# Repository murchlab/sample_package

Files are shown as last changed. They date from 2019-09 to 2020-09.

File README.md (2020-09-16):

# Sample Package v1.3

## Purchase list

1. Copper rod stock

    Superconducting 101 copper rod, Diameter = 1.5"

    https://www.mcmaster.com/8965k75

2. Screws for fastening (4 for each)

    \#4-40 Brass socket head screw, Length = 5/8"

    https://www.mcmaster.com/93465a111

3. Screws for mounting (2 for each)

    \#4-40 Brass Pan Head Phillips Screws, Length = 1"

    https://www.mcmaster.com/94070a115

4. Nuts for mounting (2 for each)

    \#4-40 Brass hex nut, Width = 1/4", Height = 3/32"

    https://www.mcmaster.com/92671a005

5. Screws for thermalization (1 for each)

    \#4-40 Brass socket head screw, Length = 1/4"

    https://www.mcmaster.com/93465a106
    
## Milling procedures

These G-code files are generated in a certain order. Particularly, I assume that the milling procedures are performed before the drilling ones.

#### The way I name the files:

1. The first letter:

        x: Stands for the top part
        y: Stands for the bottom part
        
2. The second letter:

        t: Stands for the topside of the part
        b: Stands for the bottomside of the part
        
3. Letter "c" indicates that this file is for center drills

4. The numbers indicats the tool to use.

### Top, Topside

1. Pockets: 3/32" End Mill

        xt332.txt

2. Center Drills

        xtc43.txt (Z = -0.015")
        xtc32.txt (Z = -0.135")
        xtc3mm.txt (Z = -0.135")
        
3. \#4-40 tapped holes: #43 Drill Bit

        xt43.txt (Z = -0.620")

4. \#4-40 close fit: #32 Drill Bit

        xt32.txt (Z = -0.620")

5. \#4-40 mounting holes: 3mm Drill Bit

        xt3mm.txt (Z = -0.620")
          
### Top, Bottomside

1. The pocket: 3/32" End Mill

        xb332.txt
        
### Bottom, Topside

1. Open pocket: 3/8"" End Mill

        yt38.txt

2. Pockets: 3/32" End Mill

        yt332.txt

3. Center Drills

        ytc45.txt (Z = -0.015")
        ytc43.txt (Z = -0.055")
        ytc2p3.txt (Z = -0.105")
        ytc3mm.txt (Z = -0.055")

4. Post pockets: #45 Drill Bit

        yt45.txt (Z = -0.0667")
        
5. \#4-40 tapped holes: #43 Drill Bit

        yt43.txt (Z = -0.300")
        
6. Coaxial holes: #42 Drill BIt

        yt40.txt (Z = -0.300")
        
7. \#4-40 mounting holes: 3mm Drill Bit

        yt3mm.txt (Z = -0.300")

### Bottom, Bottomside

1. Pockets: 3/32" End Mill

        yb332.txt

## Guidelines for CNC machining (Bridgeport EZTrak)

### Workflow
    
1. Design the part using SolidWorks.

2. Generate the toolpaths using the built-in SolidWorks CAM.

3. Generate the G-code files using a post processor named "EZTRAK_G.ctl". One G-code file corresponding to one toolpath only (without tool change operations).

4. Use the python scripts to modify the generated G-code files.

### Compatibility

The machine is old, which means certain G-code commands are not recognized by this machine. The known examples include:
  
1. Drilling commands like G81, G83

2. Tool radius compensation commands like G40, G41

In order to bypass these commands, we use python scripts to modify the G-code files generated by the default "Drill" and "Center Drill" operations in SolidWorks CAM.

### Milling

We do both roughing & finishing procedures.

1. Spindle

        Spindle Speed = 2400 rpm

2. Feedrates:

        XY Feedrate = 8 in/min
    
        Z Feedrate = 4 in/min
        
        Leadin Feedrate = 4 in/min
    
3. Side parameters:
    
        Allowance = 0.01 in
        
        Stepover = 80%
      
        Wedge Machining: True
      
4. Depth parameters:

    a. For roughing

        Bottom Allowance = 0 in
    
        Island Allowance = 0 in
    
        First Cut Amount = 0.02 in
    
        Max Cut Amount = 0.02 in
    
        Final Cut Amount = 0.01 in
        
    b. for finishing
    
        Allowance = 0 in
    
        First Cut Amount = 10 in
    
        Max Cut Amount = 10 in
    
        Final Cut Amount = 0 in
        
        (The value "10 in" can be as large as possible)

5. NC

        CNC Compensation: OFF
        
        (This prevents the program from producing G40 and G41 codes.)
        
### Drilling

We do centering before drilling. G-code file for both procedures are modified by the python script "modify_gcode.py". Spindle and feedrate parameters are the same as used in the milling procedures.

1. Center Drill

        Center Drill Depth = 0.015 in

2. Drill

        Add Tip Length: True
        
3. Pecking (This parameter is defined in the python file "gcode-tools.py")

        Pecking Depth = 0.050"

## Related projects

1. A new sample rack and a new copper bucket for our new fridge

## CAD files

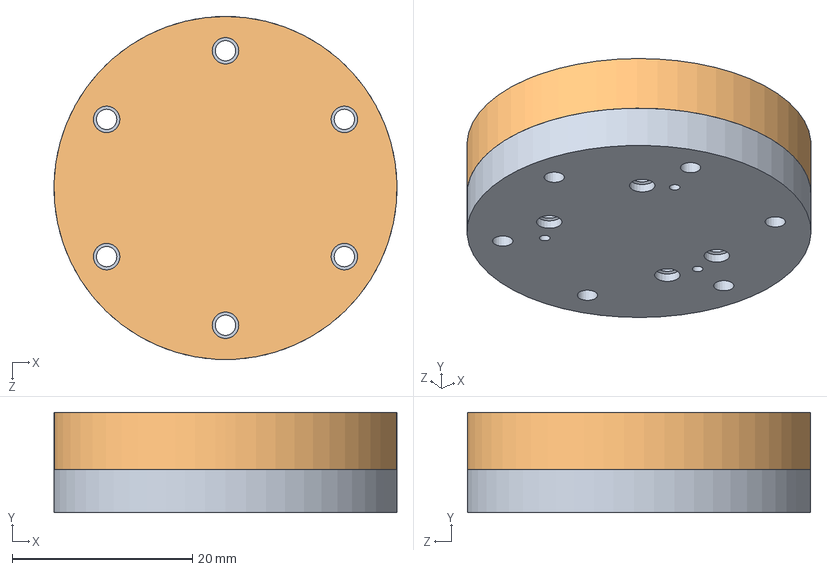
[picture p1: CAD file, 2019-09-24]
Assembly.SLDASM
38.1 x 11.1 x 38.1 mm
Bottom
Top

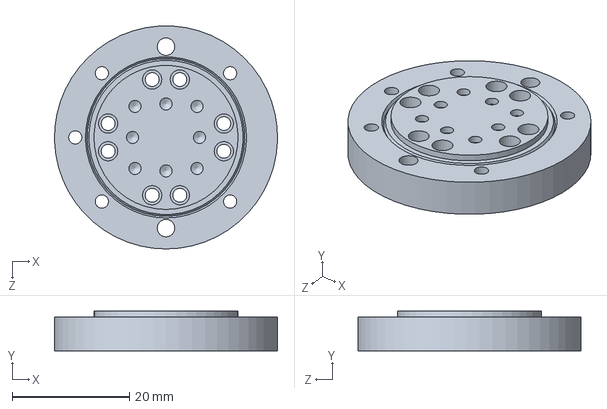
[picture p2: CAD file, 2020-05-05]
Bottom.SLDPRT
38.1 x 6.81 x 38.1 mm

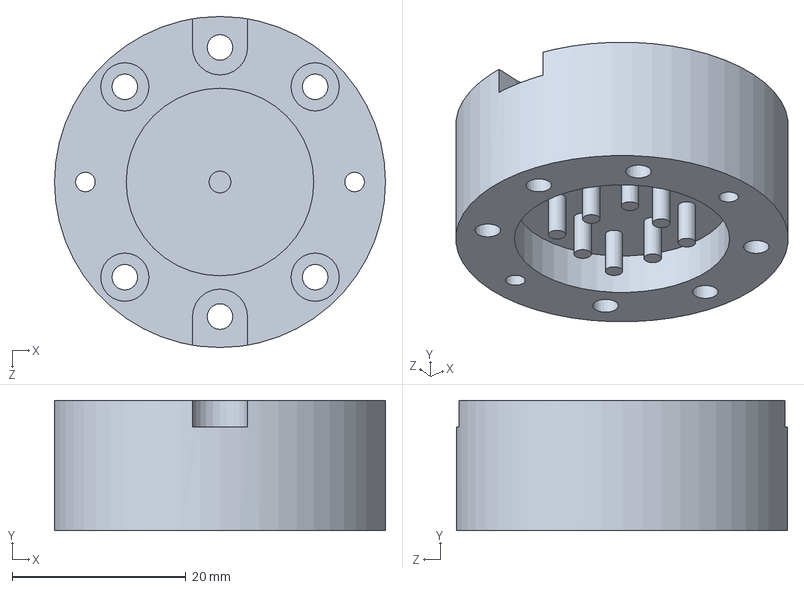
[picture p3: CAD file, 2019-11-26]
Top.SLDPRT
38.1 x 15.0 x 38.1 mm

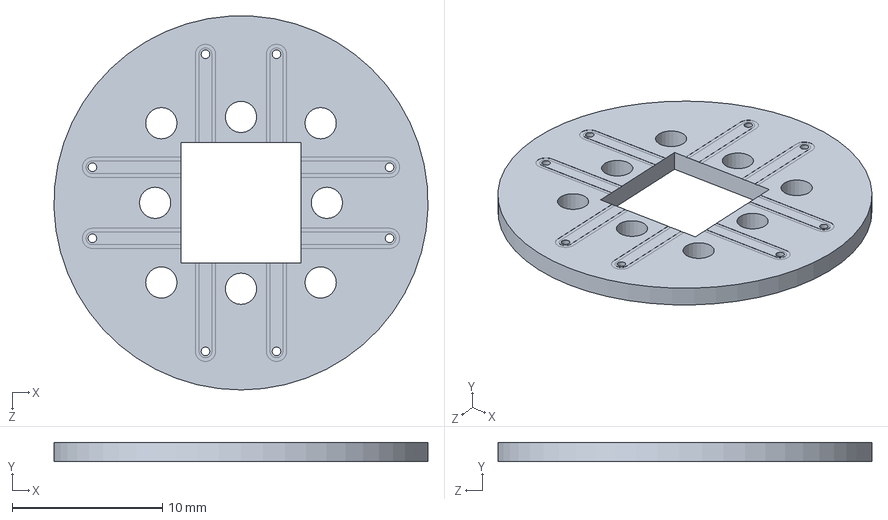
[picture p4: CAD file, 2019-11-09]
Dielectric.SLDPRT
24.9 x 1.29 x 24.9 mm

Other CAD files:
sample_package.SLDDRW

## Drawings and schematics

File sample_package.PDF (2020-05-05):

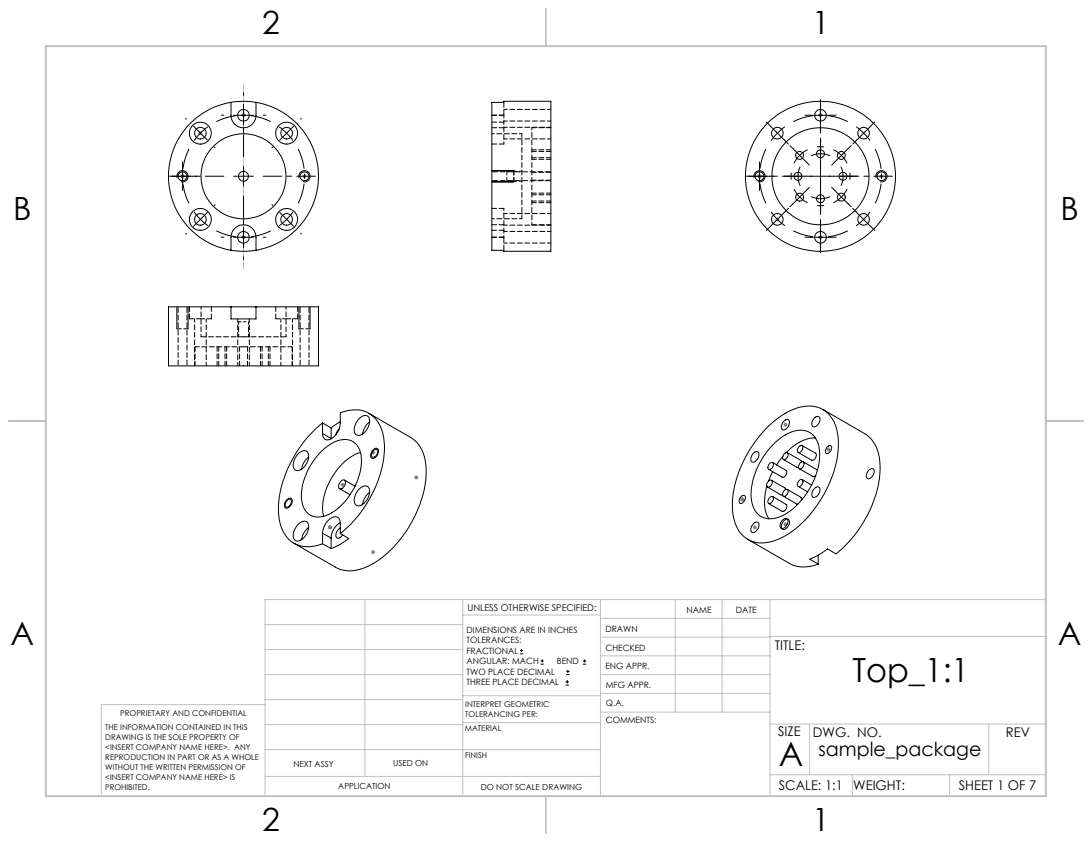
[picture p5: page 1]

UNLESS OTHERWISE SPECIFIED: | | NAME | DATE
DIMENSIONS ARE IN INCHES TOLERANCES: FRACTIONAL ANGULAR: MACH BEND TWO PLACE DECIMAL THREE PLACE DECIMAL | DRAWN

CHECKED | | | TITLE: Top_1:1

ENG APPR.
MFG APPR.

INTERPRET GEOMETRIC TOLERANCING PER: | Q.A.
MATERIAL | | SIZE A | DWG. NO. sample_package | REV

PROPRIETARY AND CONFIDENTIAL
THE INFORMATION CONTAINED IN THIS
DRAWING IS THE SOLE PROPERTY OF
<INSERT COMPANY NAME HERE>. ANY
REPRODUCTION IN PART OR AS A WHOLE
WITHOUT THE WRITTEN PERMISSION OF
<INSERT COMPANY NAME HERE> IS
PROHIBITED.

NEXT ASSY | USED ON | FINISH

APPLICATION | DO NOT SCALE DRAWING | | SCALE: 1:1 | WEIGHT: | SHEET 1 OF 7

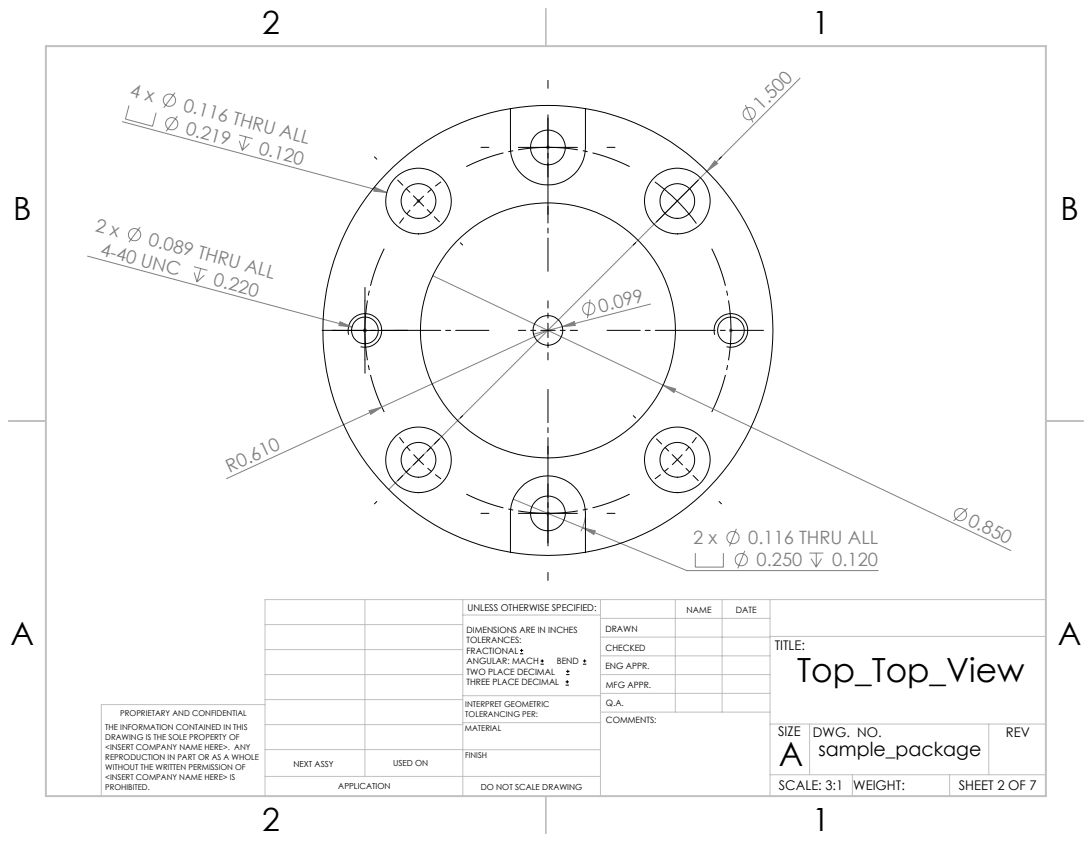
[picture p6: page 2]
2 x 0.089 THRU ALL 4-40 UNC 0.220; 4 x 0.116 THRU ALL 0.219 0.120; 0.116 THRU ALL

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

CHECKED | | | TITLE: Top_Top_View

ENG APPR.
MFG APPR.

INTERPRET GEOMETRIC TOLERANCING PER: | Q.A.
MATERIAL | | SIZE A | DWG. NO. sample_package | REV

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

NEXT ASSY | USED ON | FINISH

SCALE: 3:1 | WEIGHT:

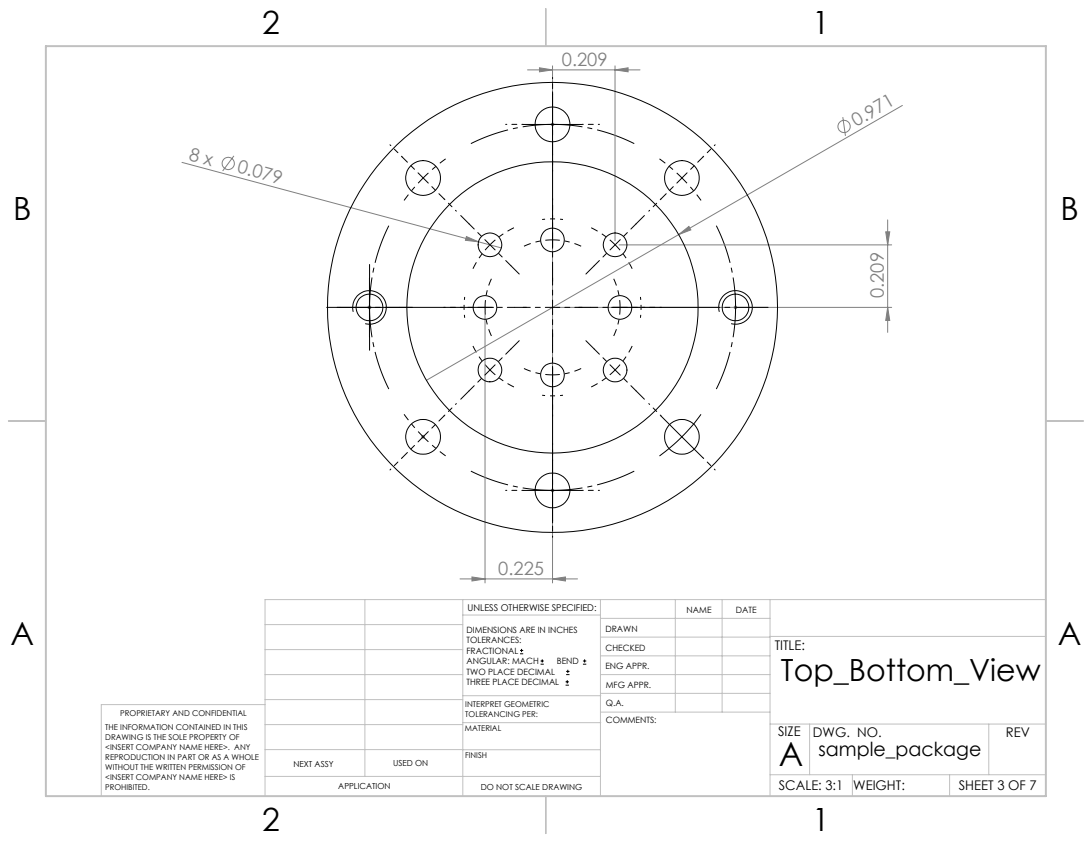
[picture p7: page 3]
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

CHECKED | | | TITLE: Top_Bottom_View

ENG APPR.
MFG APPR.

INTERPRET GEOMETRIC TOLERANCING PER: | Q.A.
MATERIAL | | SIZE A | DWG. NO. sample_package | REV

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

NEXT ASSY | USED ON | FINISH

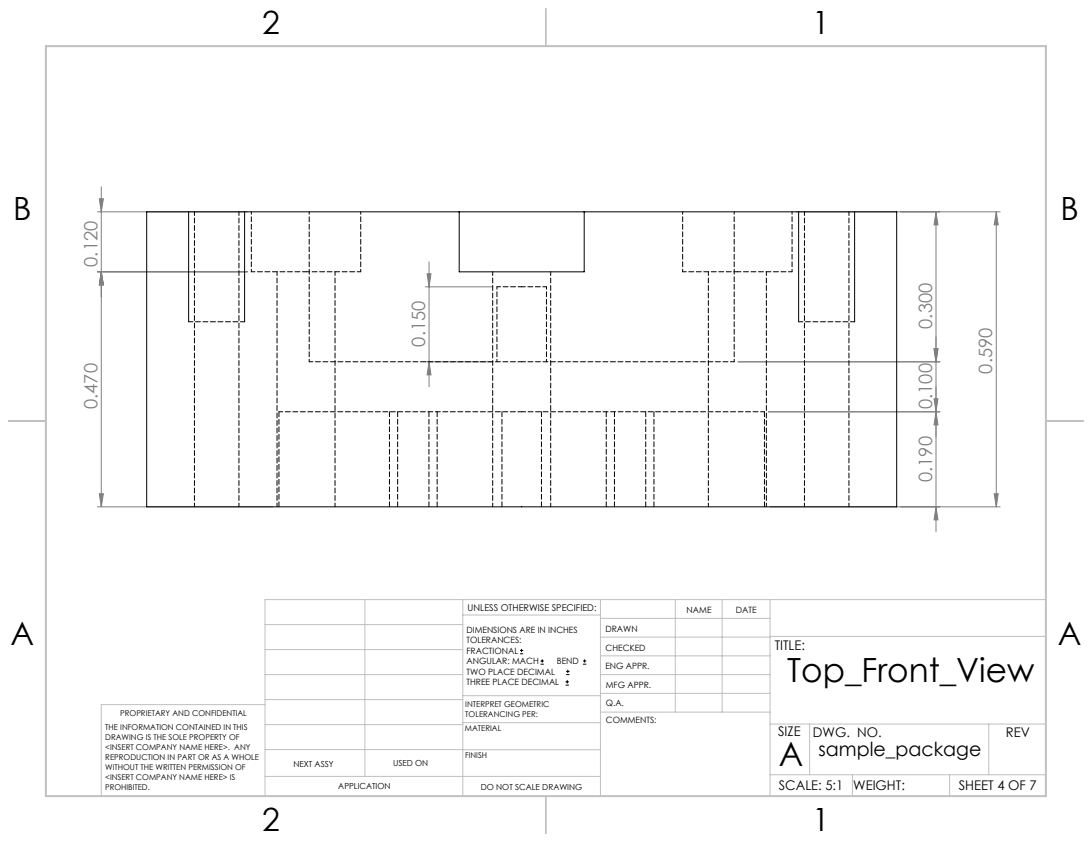
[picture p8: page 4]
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

CHECKED | | | TITLE: Top_Front_View

ENG APPR.
MFG APPR.

INTERPRET GEOMETRIC TOLERANCING PER: | Q.A.
MATERIAL | | SIZE A | DWG. NO. sample_package | REV

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

NEXT ASSY | USED ON | FINISH

SCALE: 5:1 | WEIGHT:

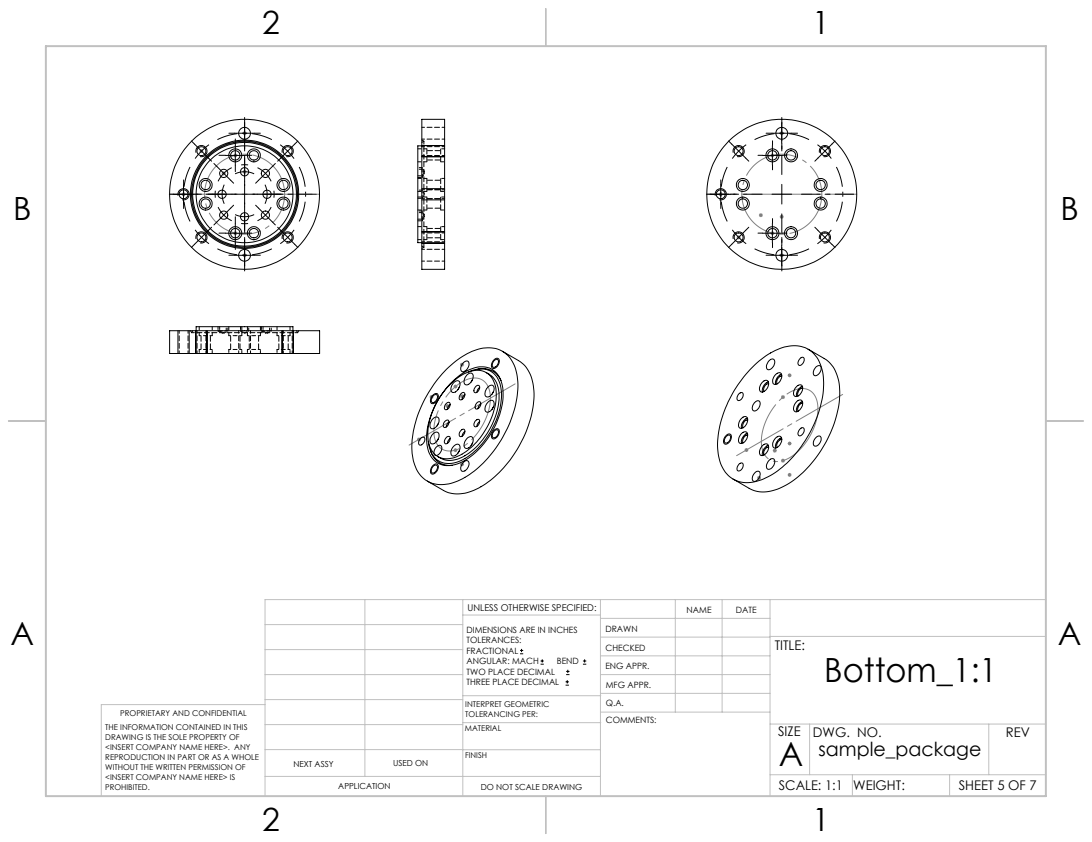
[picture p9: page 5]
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

CHECKED | | | TITLE: Bottom_1:1

ENG APPR.
MFG APPR.

INTERPRET GEOMETRIC TOLERANCING PER: | Q.A.
MATERIAL | | SIZE A | DWG. NO. sample_package | REV

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

NEXT ASSY | USED ON | FINISH

SCALE: 1:1 | WEIGHT:

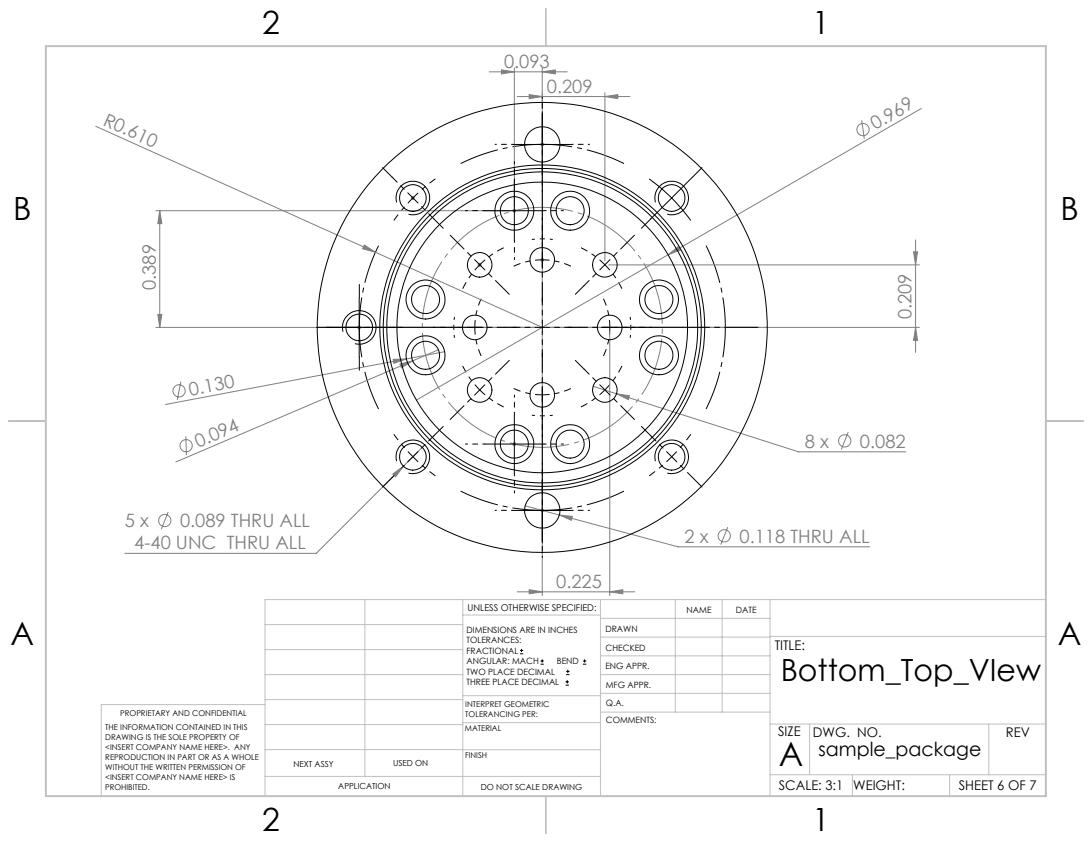
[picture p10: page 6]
0.118 THRU ALL; 0.089 THRU ALL

4-40 UNC THRU ALL

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

CHECKED | | | TITLE: Bottom_Top_VIew

ENG APPR.
MFG APPR.

INTERPRET GEOMETRIC TOLERANCING PER: | Q.A.
MATERIAL | | SIZE A | DWG. NO. sample_package | REV

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

NEXT ASSY | USED ON | FINISH

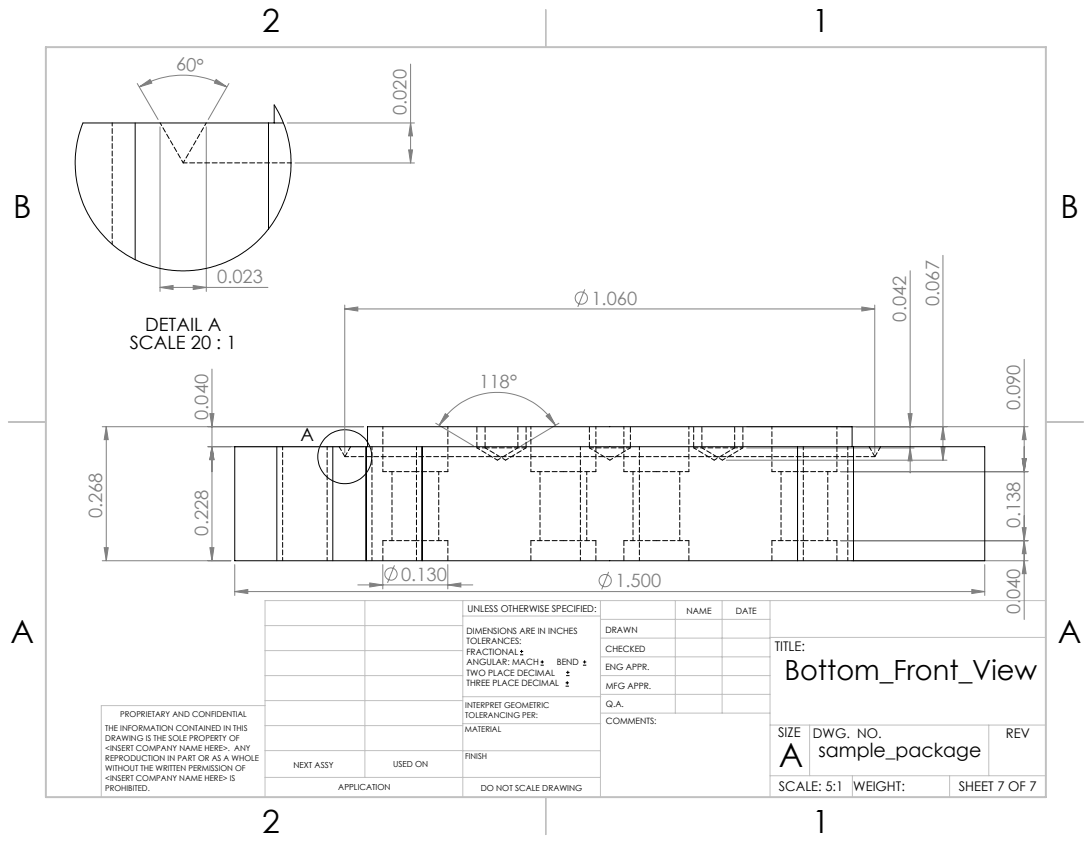
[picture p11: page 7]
DETAIL A SCALE 20 : 1

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

CHECKED | | | TITLE: Bottom_Front_View

ENG APPR.
MFG APPR.

INTERPRET GEOMETRIC TOLERANCING PER: | Q.A.
MATERIAL | | SIZE A | DWG. NO. sample_package | REV

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

NEXT ASSY | USED ON | FINISH

SCALE: 5:1 | WEIGHT:

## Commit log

2019-09-13 Add Assembly
    [Assembly.SLDASM]
2019-09-13 Added assembly.
    [Bottom.SLDPRT, Top.SLDPRT]
2019-09-15 Added Sample Mount
    [Bottom.SLDPRT]
2019-09-17 Added box mode simulation
    [Bottom.SLDPRT, Bottom.x_t, Sample_Mount.SLDPRT, Sample_Mount.x_t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]
2019-09-24 renamed Sample_Mount.SLDPRT -> Dielectric.SLDPRT
    [Dielectric.SLDPRT]
2019-09-24 Revert "Nothing"
    This reverts commit 34459a2a027ad25cef2f6041778a1a732feeca12.
    [Dielectric.SLDPRT]
2019-09-24 Modified Assembly
    [Assembly.SLDASM]
2019-09-24 Modified Dielectric
    [Dielectric.SLDPRT]
2019-09-24 Applying the "post" design in Dielectric.
    [Dielectric.SLDPRT]
2019-09-24 Changed the appearance into "polished copper"
    [Dielectric.SLDPRT]
2019-09-24 Updated the Bottom
    [Bottom.SLDPRT]
2019-09-24 Updated the Top
    [Top.SLDPRT]
2019-11-09 Merged from prototype branches
    [Bottom.SLDPRT, Dielectric.SLDPRT, Top.SLDPRT]
2019-11-09 Changed the size of the dielectric.
    [Bottom.SLDPRT, Dielectric.SLDPRT, Top.SLDPRT]
2019-11-09 Merged the hfss eigenmode simulation file from prototype branches
2019-11-10 Added the pocket for solonoid
    [Top.SLDPRT]
2019-11-11 Added holes for holding & thermalization on the top.
    [Top.SLDPRT]
2019-11-11 Added holder and thermalization holes on the bottom.
    [Bottom.SLDPRT]
2019-11-11 Modified the holes on the top.
    [Top.SLDPRT]
2019-11-11 Modified the io holes on the bottom
    [Bottom.SLDPRT, Top.SLDPRT]
2019-11-13 Added a drawing file
    [Bottom.SLDPRT, Top.SLDPRT, samplebox.SLDDRW]
2019-11-13 Changed the default precision
    [Bottom.SLDPRT, Top.SLDPRT, samplebox.SLDDRW]
2019-11-13 Generated a pdf drawing
    [Bottom.SLDPRT, Top.SLDPRT, samplebox.SLDDRW]
2019-11-13 Modified the Bottom_1:1 drawing
    [samplebox.SLDDRW]
2019-11-13 Name change: samplebox -> sample_box
    [sample_box.SLDDRW, samplebox.SLDDRW]
2019-11-13 Name change: sample_box -> sample_package
    [sample_box.SLDDRW, sample_package.SLDDRW]
2019-11-14 Multiple modifications after discussion
    [Bottom.SLDPRT, Top.SLDPRT, sample_package.SLDDRW]
2019-11-15 1) 4 x Thru holes 0.116" -> 0.118" 2) Drill hole depth 0.090" -> 0.067"" (total)
    [Bottom.SLDPRT, Top.SLDPRT, sample_package.SLDDRW]
2019-11-15 Added "Add tip length" in drilling section
2019-11-15 Modified the drill files using a python script
2019-11-15 Skipped the first fast movement when drilling
2019-11-15 Added a description of the milling procedures
2019-11-15 Created toolpaths
    [Bottom.SLDPRT, Top.SLDPRT, sample_package.SLDDRW]
2019-11-15 Generated g-code
    [Bottom.SLDPRT, Top.SLDPRT]
2019-11-15 Small modification in the drawings
    [sample_package.SLDDRW]
2019-11-15 Corrected the Z-value of bb332.txt
    [Bottom.SLDPRT]
2019-11-18 Updated the description for the Milling process
2019-11-19 Added slots for mounting screws
    [Top.SLDPRT]
2019-11-19 Modified the name of the files
    [Top.SLDPRT]
2019-11-19 Changed the order to: Drill first, then mill
    [Bottom.SLDPRT, Top.SLDPRT]
2019-11-19 Made two separate g-code files for ytc43
    [Bottom.SLDPRT]
2019-11-19 Updated the Drawings
    [sample_package.SLDDRW]
2019-11-19 Added Z information for drilling g-code files
2019-11-19 Fixed a problem in yt332.txt
    [Top.SLDPRT]
2019-11-20 Corrected the number of #4-40 tapped holes in README.md
    [sample_package.SLDDRW]
2019-11-21 Modified the milling g-code files using a new python script
2019-11-22 Used the default contour mill option in SolidWorks CAM to generate the g-code files
    [Bottom.SLDPRT, Top.SLDPRT]
2019-11-26 Modified the milling procedures
2019-11-26 Inner Diameter 0.970" -> 0.971"
    [Top.SLDPRT]
2019-11-26 Coaxial holes #43 -> 2.3mm
    [Bottom.SLDPRT]
2019-11-26 Modified the toolpath
    [Bottom.SLDPRT, Top.SLDPRT]
2019-11-26 Regenerated the G-code files
    [Bottom.SLDPRT, Top.SLDPRT]
2019-11-26 Spingdle speed 2358 -> 2400
    [Bottom.SLDPRT]
2019-11-27 Added the 3/8" milling information
2019-11-28 Added 3/8" milling g-code file
    [Bottom.SLDPRT]
2020-05-05 yt2p3 -> yt40
    [Bottom.SLDPRT, sample_package.SLDDRW]
